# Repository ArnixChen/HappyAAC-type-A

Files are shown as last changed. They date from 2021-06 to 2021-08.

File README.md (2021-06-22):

# HappyAAC-type-A
## An open-source main-board to make AAC device makers Happy ;)
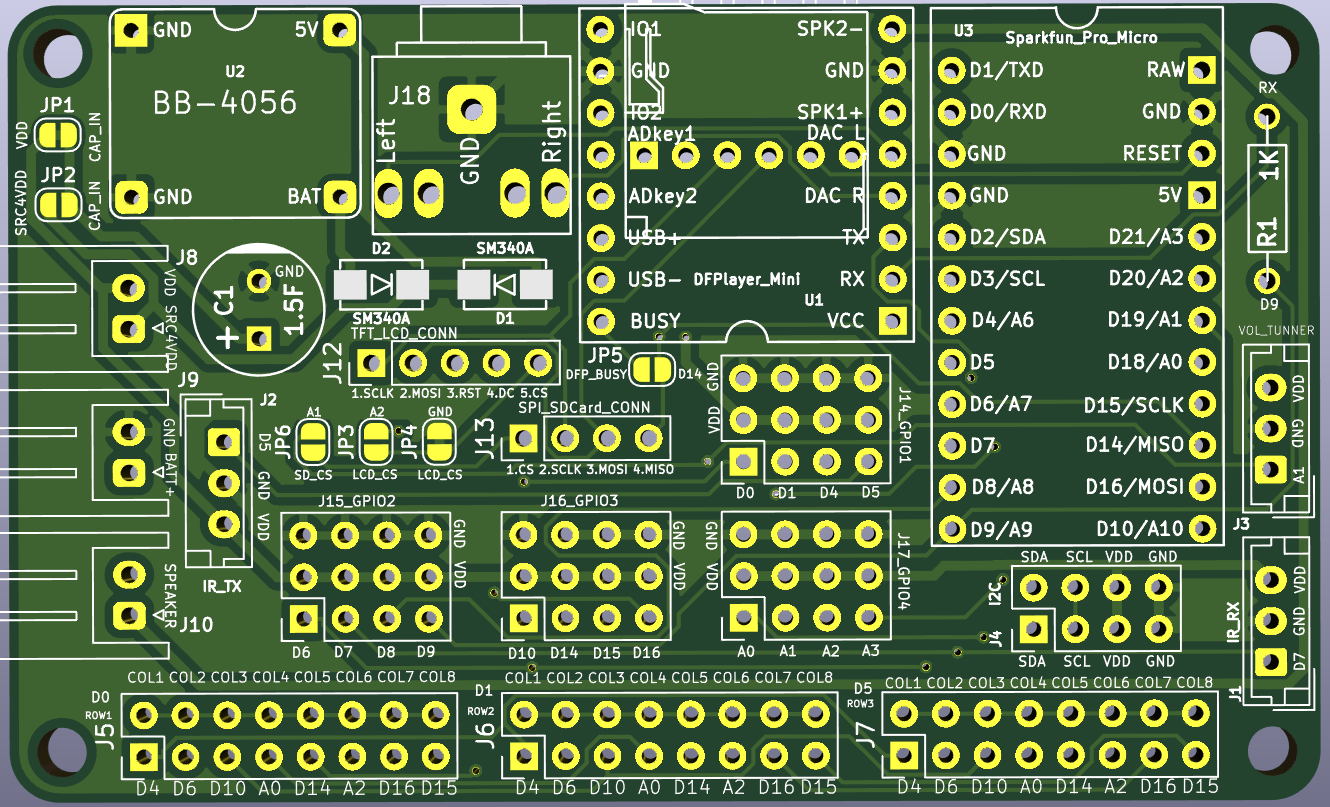
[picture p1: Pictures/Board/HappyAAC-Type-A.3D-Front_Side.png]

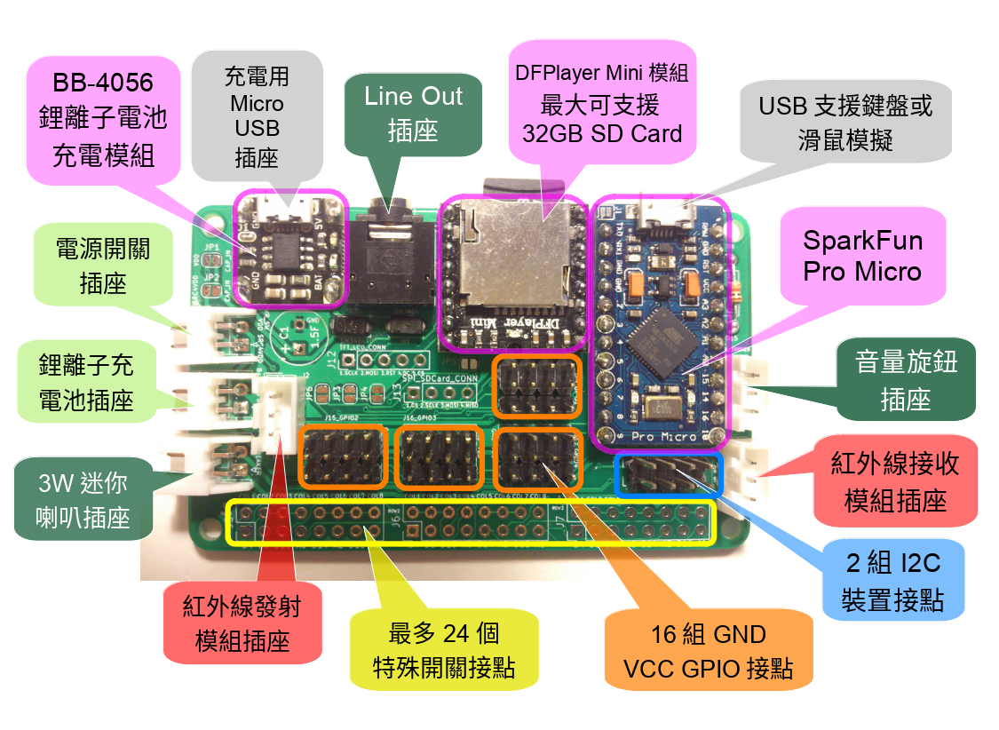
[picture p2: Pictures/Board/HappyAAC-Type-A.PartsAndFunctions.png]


## HappyAAC type A
#### 尺寸 8cm x 5cm 角落圓孔直徑 2.86mm
#### 它是一塊針對AAC溝通需求設計的開放電路板,使用者只要把必要的元件焊上電路板,就可以開始動手實作各種功能,免去手工連接大量線路的困難。

1. 使用 Sparkfun Pro Micro控制板, 支援鍵盤或滑鼠模擬功能
2. 內建 BB-4056 鋰電池充電模組線路,有插座可接鋰池及充電
3. 內建 DFPlayer Mini MP3 模組線路,內含一組音訊Line Out 用的插座,可接擴音喇叭,另有一組最大3W迷喇叭接插座
4. 一組音量旋鈕插座
5. 支援最多24個按鈕或特殊開關接點(沒有與其他功能衝突時)
6. 兩組獨立I2C裝置接點
7. 紅外線接收接座, 可以接遙控訊號
8. 紅外線發射接座,可以遙控其他的裝置
9. 留有16組GPIO +VCC+GND 接點,滿足特殊用途的需求
10. 它使用KiCad (open source)電路軟體設計, 並提供原始檔, 可以自己修改設計。

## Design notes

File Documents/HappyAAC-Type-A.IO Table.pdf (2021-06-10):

## IO使用表

Page 1

模組 PIN | Pro Micro 腳位代號 | PINs can do Interrupt wakeup | PINs can do Software Serial | ICSP 功能 | Keypad 功能 | DFPlayer Mini | Volume Tunner conn | I2C conn | IR Receiver conn | IR Transmitter conn | TFT LCD conn | SDCard Conn
1 | D1/TXD | D1 | | | ROW2
2 | D0/RXD | D0 | | | ROW1
3 | GND
4 | GND
5 | D2/SDA | D2 | | | | | | 1 SDA
6 | D3/SCL | D3 | | | | | | 2 SCL
7 | D4/A6 | | | | COL1
8 | D5 | | | | ROW3 | | | | | 1 IR_SEND
9 | D6/A7 | | | | COL2
10 | D7 | D7 | | | | | | | 1 IR_RECV
11 | D8/A8 | | D8 | | | DFP_TX
12 | D9/A9 | | D9 | | | DFP_RX
13 | D10/A10 | | D10 | | COL3
14 | D16/MOSI | | D16 | 4 MOSI | COL7 | | | | | | 4 LCD_MOSI | 3 SD_MOSI
15 | D14/MISO | | D14 | 1 MISO | COL5 | DFP_BUSY | | | | | | 4 SD_MISO
16 | D15/SCLK | | D15 | 3 SCLK | COL8 | | | | | | 3 LCD_SCLK | 2 SD_SCLK
17 | D18/A0 | | | | COL4
18 | D19/A1 | | | | | | 1 VOLUME_TUNNER | | | | | 1 SD_CS
19 | D20/A2 | | | | COL6 | | | | | | 7 LCD_CS
20 | D21/A3 | | | | | | | | | | 6 LCD_DC
21 | VCC | | | 2 VDD | | | 3 VDD | 3 VDD | 3 VDD | 3 VDD | 2 VDD | 5 VDD
22 | RESET | | | 5 RESET | e | | | | | | 5 RST
23 | GND | | | 6 GND | | | 2 GND | 4 GND | 2 GND | 2 GND | 1 GND | 6 GND
24 | RAW

## 表示未使用

Updated on 2021.0611

## 獨家使用,沒有衝突問題 有衝突, 只能擇一使用 有衝突, 只能擇一使用,但其中一方使用率低

## HappyAAC-Type-A-2c IO使用表

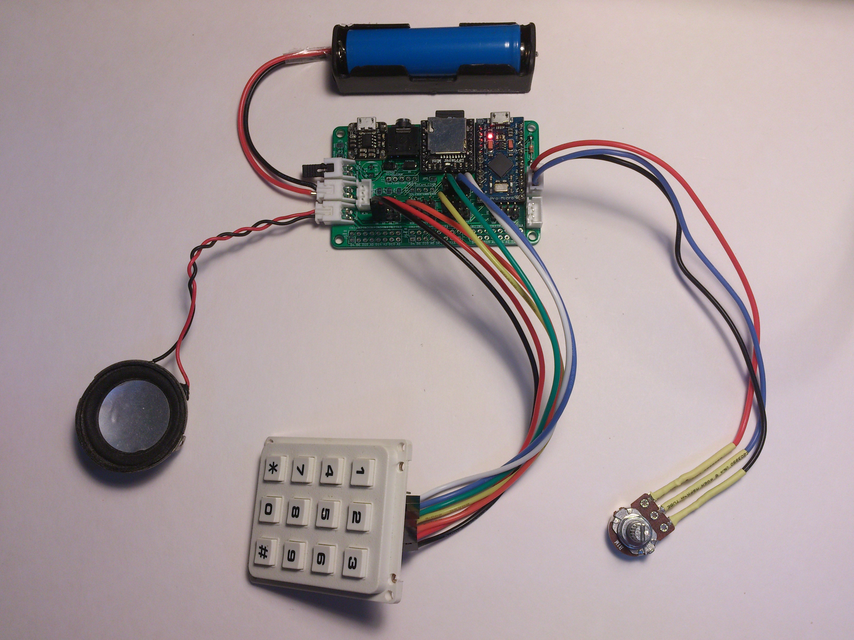
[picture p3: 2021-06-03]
Pictures/Application_Examples/phoneBox/Example_of_phoneBox.jpg

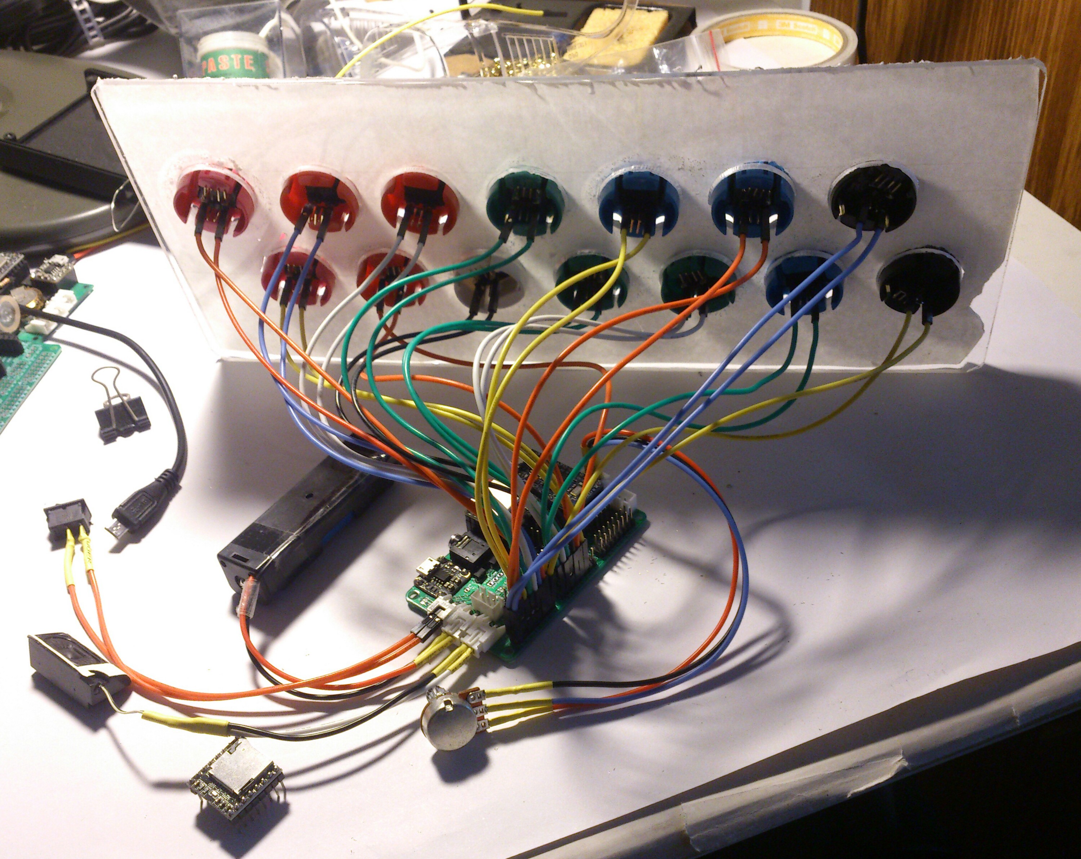
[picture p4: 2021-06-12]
Pictures/Application_Examples/Electric_Recorder/Electric_Recorder2.jpg

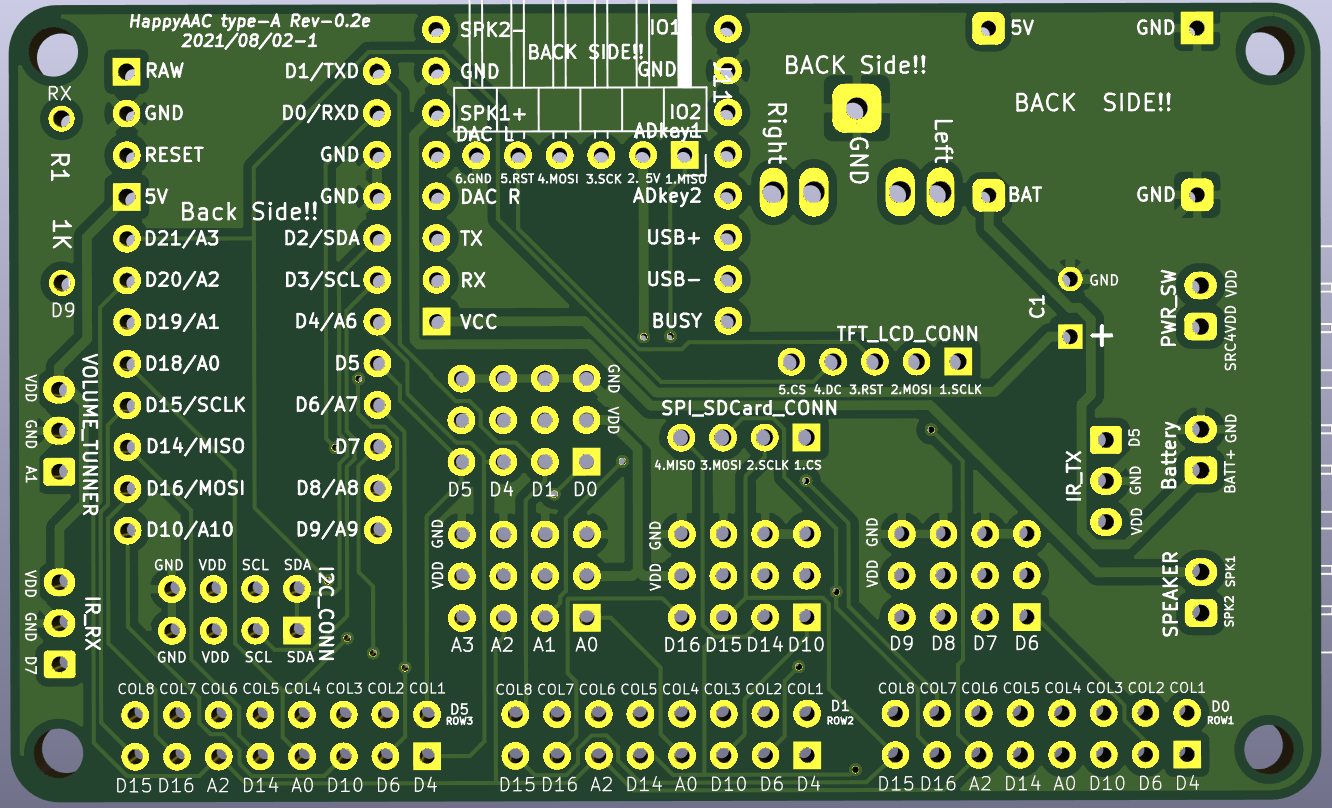
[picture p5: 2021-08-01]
Pictures/Board/HappyAAC-Type-A.3D-Back-Side.png

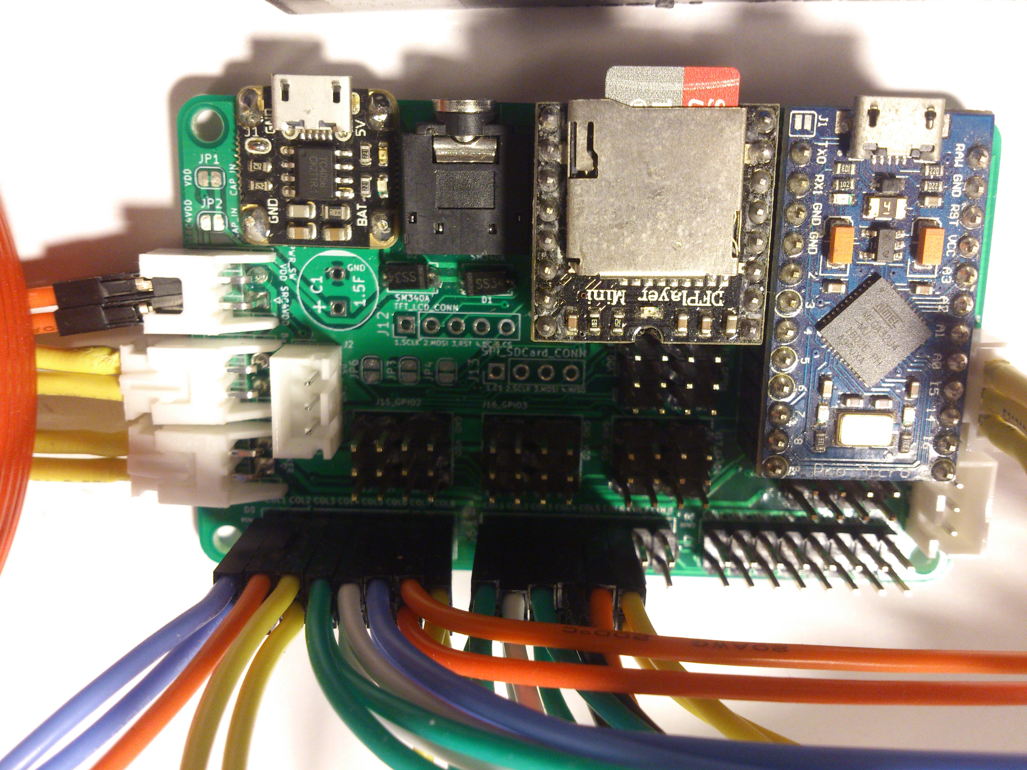
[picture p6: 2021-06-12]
Pictures/Application_Examples/Electric_Recorder/Electric_Recorder3.jpg

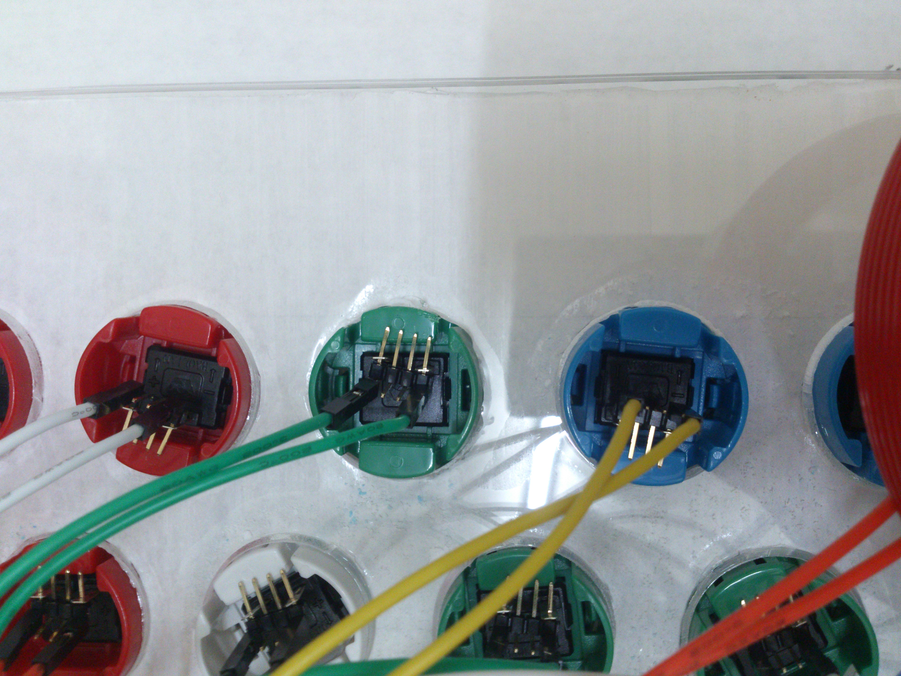
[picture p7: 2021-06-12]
Pictures/Application_Examples/Electric_Recorder/Eletric_Recorder4.jpg

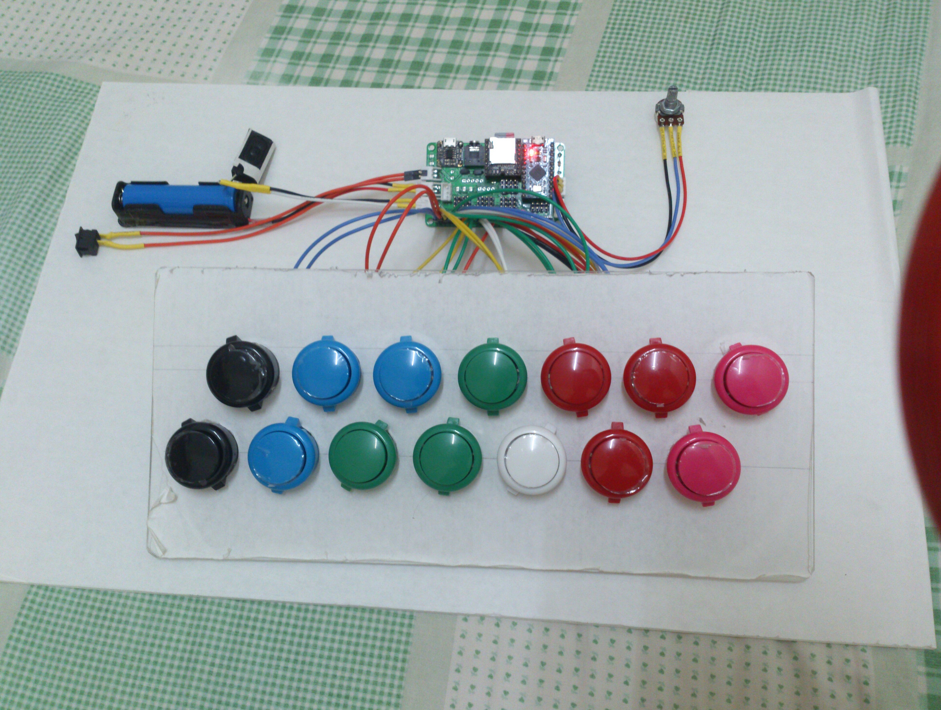
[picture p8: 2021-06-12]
Pictures/Application_Examples/Electric_Recorder/Electric_Recorder1.jpg

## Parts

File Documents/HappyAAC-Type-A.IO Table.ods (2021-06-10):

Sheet: IO使用表
模組 PIN | MCU 腳位 | Pro Micro 腳位代號 | PINs can do Interrupt wakeup | PINs can do Software Serial | ICSP 功能 | Keypad 功能 | DFPlayer Mini | Volume Tunner conn | I2C conn | IR Receiver conn | IR Transmitter conn | TFT LCD conn | SDCard Conn
1 |  | D1/TXD | D1 |  |  | ROW2
2 |  | D0/RXD | D0 |  |  | ROW1
3 |  | GND
4 |  | GND
5 |  | D2/SDA | D2 |  |  |  |  |  | 1 SDA
6 |  | D3/SCL | D3 |  |  |  |  |  | 2 SCL
7 |  | D4/A6 |  |  |  | COL1
8 |  | D5 |  |  |  | ROW3 |  |  |  |  | 1 IR_SEND
9 |  | D6/A7 |  |  |  | COL2
10 |  | D7 | D7 |  |  |  |  |  |  | 1 IR_RECV
11 |  | D8/A8 |  | D8 |  |  | DFP_TX
12 |  | D9/A9 |  | D9 |  |  | DFP_RX
13 |  | D10/A10 |  | D10 |  | COL3
14 |  | D16/MOSI |  | D16 | 4 MOSI | COL7 |  |  |  |  |  | 4 LCD_MOSI | 3 SD_MOSI
15 |  | D14/MISO |  | D14 | 1 MISO | COL5 | DFP_BUSY |  |  |  |  |  | 4 SD_MISO
16 |  | D15/SCLK |  | D15 | 3 SCLK | COL8 |  |  |  |  |  | 3 LCD_SCLK | 2 SD_SCLK
17 |  | D18/A0 |  |  |  | COL4
18 |  | D19/A1 |  |  |  |  |  | 1 VOLUME_TUNNER |  |  |  |  | 1 SD_CS
19 |  | D20/A2 |  |  |  | COL6 |  |  |  |  |  | 7 LCD_CS
20 |  | D21/A3 |  |  |  |  |  |  |  |  |  | 6 LCD_DC
21 |  | VCC |  |  | 2 VDD |  |  | 3 VDD | 3 VDD | 3 VDD | 3 VDD | 2 VDD | 5 VDD
22 |  | RESET |  |  | 5 RESET | e |  |  |  |  |  | 5 RST
23 |  | GND |  |  | 6 GND |  |  | 2 GND | 4 GND | 2 GND | 2 GND | 1 GND | 6 GND
24 |  | RAW
 |  |  | 表示未使用
 |  |  | 獨家使用,沒有衝突問題
 |  |  | 有衝突, 只能擇一使用
 |  |  | 有衝突, 只能擇一使用,但其中一方使用率低
 |  |  |  |  |  | HappyAAC-Type-A-2c IO使用表 |  |  |  |  | Updated on 2021.0611

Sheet: Bill Of Materials
編號 | 數量 | 參考記號 | 元件名稱 | 參考單價 | 總價 | 參考來源 | 說明
1 | 1 | U1 | DFPlayer Mini (非YX5200-24SS) | 63 | 63 | 露天 宇倉電子 Allen_6833 | 非YX5200-24SS版有支援 Total Folders 功能,但反應速度較 YX5200-24SS 慢
2 | 1 | U2 | BB-4056 | 15 | 15 | 露天 blkbox.me blackboxstudio
3 | 1 | U3 | Sprakfun Pro Micro 5v/16MHz | 150 | 150 | 露天 鈺瀚網舖 yuhhann_online
4 | 1 | R1 | 1KΩ 電阻 | 0.2 | 0.2 | 今華電子
5 | 1 | C1 | 1.5F 電容 | 33 | 33 | 不確定 | 非必要零件(供電不穩時才考慮使用)
6 | 3 | J1,J2,J3 | 2.50mm JST 01x03pin Vertical 公 | 2 | 6 | 今華電子
7 | 1 | J4 | 2.54mm PinHeader 02x04pin 180度 |  | 0 | 今華電子 | I2C
8 | 3 | J5,J6,J7 | 2.54mm PinHeader 02x08pin 90度 |  | 0 | 今華電子 | For Keypad Connector
9 | 1 | J8 | 2.50mm JST 01x02pin Horizontal 公 | 1 | 1 | 今華電子 | Speaker Connector
10 | 1 | J14 | 2.50mm JST 01x02pin Horizontal 公 | 1 | 1 | 今華電子 | Power Switch Connector
11 | 1 | J15 | 2.50mm JST 01x02pin Horizontal 公 | 1 | 1 | 今華電子 | Battery Connector
12 | 1 | J9 | 3.5mm Stereo Audio Jack 4pin+Ground | 10 | 10 | 今華電子 | Audio Jack
13 | 1 | J11 | 2.54mm 01x06pin 排針母座 | 3 | 3 | 今華電子 | ICSP Connector
14 | 1 | J12 | 2.54mm 01x05pin 排針母座 | 2.5 | 2.5 | 今華電子 | SPI connector for TFT LCD
15 | 4 | J13,J17,J19,J21 | 2.54mm PinHeader 03x04pin 180度 |  | 0 | 今華電子 | General GPIO Connector
16 | 2 | D1,D2 | SM340A | 5.4 | 10.8 | 露天 ju_el | 防止電流倒灌造成逆向充電
17 | 1 | J18 | Stereo Audio Jack Socket | 10 | 10 | 今華電子 | Line out 插座
18 | 1 | PCB | HappyAAC type A PCB | 60 | 60 |  | 無鉛鍍錫拼版與不拼版價差可能1倍
19 |  |  |  |  | 0
20 |  |  |  |  | 0
21 |  | 價格需要再調查 |  |  | 0
 |  |  |  | 合計 | 366.5

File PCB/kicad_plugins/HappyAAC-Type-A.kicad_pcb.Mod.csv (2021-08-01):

Reference | RefVisible | Value | ValVisible | xPos | yPos | Orientation | LayerName | IsFlipped
U2 | True | BB-4056 | True | 73990200.0 | 34036000.0 | 0.0 | F.Cu | False
U1 | True | DFPlayer_Mini | True | 105105000.0 | 35941000.0 | 180.0 | F.Cu | False
J11 | True | ICSP | True | 98856800.0 | 35991800.0 | 90.0 | F.Cu | False
J10 | True | SPEAKER | True | 67445400.0 | 61465900.0 | 270.0 | F.Cu | False
J9 | True | Batt | True | 67445400.0 | 52767300.0 | 270.0 | F.Cu | False
J8 | True | PWR_SW | True | 67445400.0 | 44005200.0 | 270.0 | F.Cu | False
U3 | True | Sparkfun_Pro_Micro | True | 125248000.0 | 43586400.0 | 0.0 | F.Cu | False
J18 | True | AudioJack | True | 88366600.0 | 33172400.0 | 270.0 | F.Cu | False
C1 | True | 1.5F | True | 75387200.0 | 45351700.0 | 90.0 | F.Cu | False
J1 | True | IR_RX | True | 137004000.0 | 66941100.0 | 90.0 | F.Cu | False
J2 | True | IR_TX | True | 73228200.0 | 53403500.0 | 270.0 | F.Cu | False
J3 | True | VOL_TUNNER | True | 137004000.0 | 55206900.0 | 90.0 | F.Cu | False
R1 | True | 1K | True | 136804000.0 | 38705700.0 | 90.0 | F.Cu | False
J4 | True | I2C | True | 122542000.0 | 64912200.0 | 90.0 | F.Cu | False
J5 | True | ROW1 | True | 68306400.0 | 72585900.0 | 90.0 | F.Cu | False
J14_GPIO1 | True | Conn_03x04_Odd_Even_VSG | True | 104877000.0 | 52123300.0 | 90.0 | F.Cu | False
J15_GPIO2 | True | Conn_03x04_Odd_Even_VSG | True | 78066900.0 | 61645800.0 | 90.0 | F.Cu | False
J16_GPIO3 | True | Conn_03x04_Odd_Even_VSG | True | 91471900.0 | 61633100.0 | 90.0 | F.Cu | False
J17_GPIO4 | True | Conn_03x04_Odd_Even_VSG | True | 104877000.0 | 61633100.0 | 90.0 | F.Cu | False
D1 | True | SM340A | True | 90384300.0 | 43841000.0 | 180.0 | F.Cu | False
D2 | True | SM340A | True | 82854800.0 | 43841000.0 | 0.0 | F.Cu | False
J12 | True | TFT_LCD | True | 82219800.0 | 48602900.0 | 90.0 | F.Cu | False
JP1 | True | SolderJumper_2_Bridged | True | 63182500.0 | 34683700.0 | 0.0 | F.Cu | False
JP2 | True | SolderJumper_2_Open | True | 63220600.0 | 38938200.0 | 0.0 | F.Cu | False
JP3 | True | SolderJumper_2_Open | True | 82510600.0 | 53403500.0 | 90.0 | F.Cu | False
JP4 | True | SolderJumper_2_Bridged | True | 86357400.0 | 53403500.0 | 90.0 | F.Cu | False
JP5 | True | SolderJumper_2_Open | True | 99326700.0 | 49034700.0 | 0.0 | F.Cu | False
J13 | True | SDCard_Conn | True | 91478100.0 | 53213000.0 | 90.0 | F.Cu | False
JP6 | True | SolderJumper_2_Open | True | 78663800.0 | 53403500.0 | 90.0 | F.Cu | False
J6 | True | ROW2 | True | 91468700.0 | 72585900.0 | 90.0 | F.Cu | False
J7 | True | ROW3 | True | 114631000.0 | 72585900.0 | 90.0 | F.Cu | False

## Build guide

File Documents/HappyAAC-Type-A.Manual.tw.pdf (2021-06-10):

# HappyAAC type A

## 說明書

2021/06/09 更新

免責聲明： HappyAAC type A, 以下簡稱 HappyAAC 。
HappyAAC 之設計僅在於提供大眾一個設計之參考範例、應用之構思基 礎。任何運用 HappyAAC 設計的人士，必須自行承擔一切風險。

HappyAAC 的開發者不會負責任何運用 HappyAAC 設計而導致之損 失，亦不會作出任何默認的擔保。 HappyAAC 不保證其設計正確無誤 , 也不保證其設計不存在風險。我們不對運用 HappyAAC 者的財產、身、 心損害負有賠償責任。

## 1. HappyAAC type A 介紹

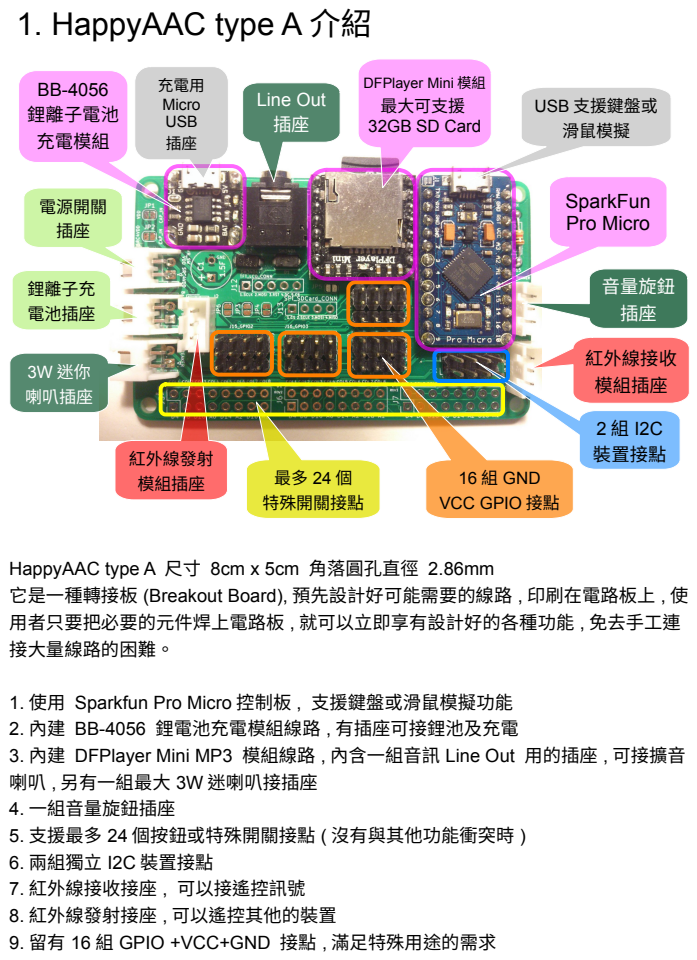
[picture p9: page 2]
SparkFun Pro Micro; 音量旋鈕 插座; 紅外線接收 模組插座; 紅外線發射; 裝置接點; 模組插座; 特殊開關接點; 電源開關 插座; 鋰離子充 電池插座; 3W 迷你 喇叭插座; Line Out 插座; BB-4056 鋰離子電池 充電模組; 充電用 Micro USB 插座; USB 支援鍵盤或 滑鼠模擬

DFPlayer Mini 模組
最大可支援
32GB SD Card

16 組 GND
VCC GPIO 接點

HappyAAC type A 尺寸 8cm x 5cm 角落圓孔直徑 2.86mm
它是一種轉接板 (Breakout Board), 預先設計好可能需要的線路 , 印刷在電路板上 , 使
用者只要把必要的元件焊上電路板 , 就可以立即享有設計好的各種功能 , 免去手工連
接大量線路的困難。

1. 使用 Sparkfun Pro Micro 控制板 , 支援鍵盤或滑鼠模擬功能
2. 內建 BB-4056 鋰電池充電模組線路 , 有插座可接鋰池及充電
3. 內建 DFPlayer Mini MP3 模組線路 , 內含一組音訊 Line Out 用的插座 , 可接擴音
喇叭 , 另有一組最大 3W 迷喇叭接插座
4. 一組音量旋鈕插座
5. 支援最多 24 個按鈕或特殊開關接點 ( 沒有與其他功能衝突時 )
6. 兩組獨立 I2C 裝置接點
7. 紅外線接收接座 , 可以接遙控訊號
8. 紅外線發射接座 , 可以遙控其他的裝置
9. 留有 16 組 GPIO +VCC+GND 接點 , 滿足特殊用途的需求

1. SparkFun Pro Micro 5v,16Mhz x1
2. DFPlayer Mini x1
3. BB-4056 鋰電池充電模組 x1
4. SM340A schottky barrier rectifiers SMD x2
5. 1K 歐姆電阻 x1
6. JST-XH 2-pin 連接器 ( 水平 或 垂直 可自選 ) 公頭 x3
7. JST-XH 2-pin 連接器 母頭 x3
8. JST-XH 3-pin 連接器 垂直 公頭 x3
9. Phone Jack 耳機插座 3.5mm 5-pin x1
10. 間距 2.54mm 40-pin 單排排針母座 易折型 x1
11. 間距 2.54mm 40-pin 雙排排針 (180 度 ) 易折型 x2
12. 最大 3 W 的 4 或 8 歐姆 喇叭 x1
13. JST-XH 端子頭 x15
14. MicroSD Card x1 (SD 卡大小 , 視使用的音檔總容量而定）
15. 開關 ( 電源用類型不拘 ) x1

16.18650 鋰離子電池 ( 為了安全 , 務必使用大廠電池 ) x1

17. 18650 電池槽 x1

PS. 第 6 項、第 8 項 , 不一定非使用 JST-XH 連接器不可 , 也可以用 2.54mm 排針代替。 只是這樣就沒有防呆的保護功能 ( 開關插座及喇叭插座沒有極性的問題 , 可以不用 JST-XH)
如果有意使用 JST-XH 連接器的話 , 強烈建議 - 要準備一支像 KELY YS-09A/E 的 JST-XH
專用壓接鉗 , 不然使用一般的工具 , 想要把 JST 端子壓好是很困難的。

## 3. HappyAAC type A 零件表

鋰電池本身就存在可能發生
爆炸的風險，使用者務必慎
選品質可靠的廠牌來源，並
在使用上特別小心。

## 4. HappyAAC type A 的正反面辨識

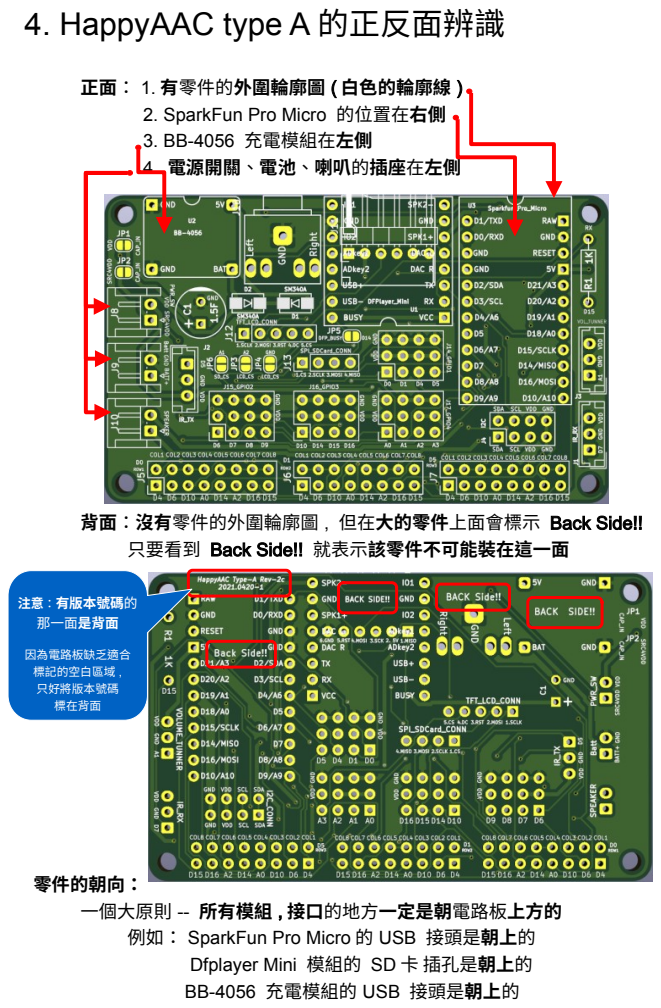
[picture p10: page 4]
注意：有版本號碼的 那一面是背面; 因為電路板缺乏適合 標記的空白區域 , 只好將版本號碼 標在背面

正面： 1. 有零件的外圍輪廓圖 ( 白色的輪廓線 )

2. SparkFun Pro Micro 的位置在右側
3. BB-4056 充電模組在左側
4. 電源開關、電池、喇叭的插座在左側

背面：沒有零件的外圍輪廓圖 , 但在大的零件上面會標示 Back Side!!
只要看到 Back Side!! 就表示該零件不可能裝在這一面

零件的朝向：
一個大原則 -- 所有模組 , 接口的地方一定是朝電路板上方的
例如： SparkFun Pro Micro 的 USB 接頭是朝上的

Dfplayer Mini 模組的 SD 卡 插孔是朝上的
BB-4056 充電模組的 USB 接頭是朝上的

## 5.HappyAAC type A 焊接順序 part I

1. 正面 SM340A schottky barrier rectifiers SMD
1. 先在 pad 塗上助焊劑。

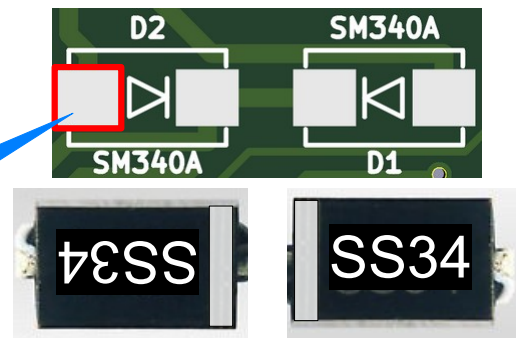
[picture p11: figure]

(pad: 指電路板上用來接通元件與電路板的表面區域 , 上焊錫的區域）
2. 將 SM340A 依圖示方向擺置在 pad 上 ( 有白線的那一側要朝中央 )
3. 烙鐵尖端沾少許焊錫 , 將沾有焊錫的部位靠向其中一顆 SM340A 的 側邊金屬與 pad 交界的地方 ( 最好用空出來的另一隻手拿夾子夾住 SMA340A, 使用它不會一碰就移位 ), 待焊錫被吸入 SM340A 底部 , 並覆蓋 側邊金屬部位 , 即完成該側的焊接 , 繼續完成同顆另一端的焊接。
4. 依同樣 1~3 步驟完成另一顆 SMA340A 的焊接。
2. 背面 ICSP 接頭 ( 正面電路板上畫有 ICSP 針腳輪廓圖是錯的 , 不要理它 , 應該畫在背面 )
1. 取出 40-pin 單排排針母座 , 用尖嘴鉗折出長度 6-pin 的片段。

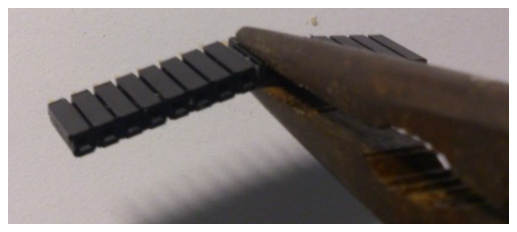
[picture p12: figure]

2. 剪下一片雙面膠貼滿排針母座的其中一面 , 用刀片割去多餘的雙面膠。
3. 利用桌面 , 稍微施力將接腳（折向貼有雙面膠的一側）折彎 90 度。
4. 撕開雙面膠 , 將此 6-pin ICSP 接頭貼在電路板背面的 ICSP 位置
針腳一一插入 6.GND 5.RST 4.MOSI 3.SCK 2.5V 1.MISO 標示上方
的焊孔。

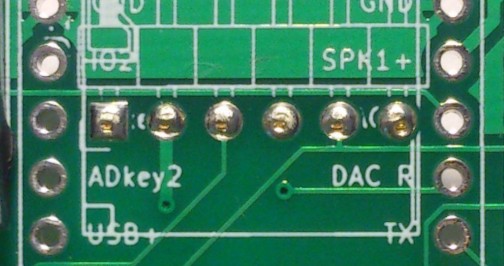
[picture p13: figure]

5. 在電路板背面 , 將每支針腳與焊孔相接部位確實焊接。
3. 正面 右上角 1K 歐姆電阻
4. BB-4056 鋰電池充電模組
注意：安裝前 , 要注意核對電路板上的輪廓圖 ,USB 接口朝向要跟輪廓圖 的半圓形方向一致 , 如果裝錯了 , 通電時可能會把模組燒壞。
5. 正面 Line Out 插座
1. 用斜口鉗將插座底部小圓突起一一剪去 ( 如此 , 插座在電路板上伸出來 的接腳才會夠長 ), 然後再插上電路板進行焊接。

pad

※ 如果想要以後可以把 Pro Micro 及 DFPlayer Mini 拆下來再利用 , 可以把下面的
步驟 2 改成：在電路板 上原本給 Pro Micro 及 DFPlayer Mini 用的焊孔上 , 各焊 兩排排針母座 , 再將已焊好針腳的 Pro Micro 及 DFPlayer Mini 插到排針母
座上。其中
SparkFun Pro Micro 要用 12-pin 的排針母座 x2
DFPlayer Mini 要用 8-pin 的排針母座 x2

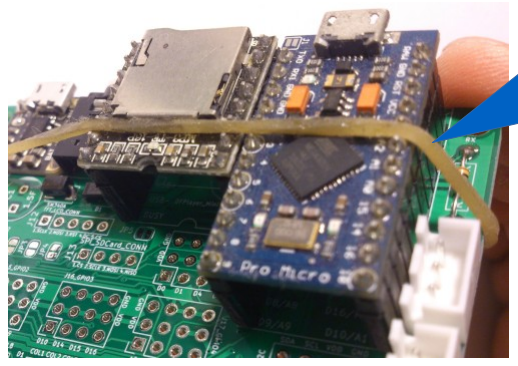
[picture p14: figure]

5. SparkFun Pro Micro 5v,16Mhz
注意：安裝前 , 要注意核對電路板上的輪廓圖 ,USB 接口朝向要跟輪廓圖的半 圓形方向一致 , 如果裝錯了 , 通電時可能會把模組燒壞。
1. 為 SparkFun Pro Micro 的兩側焊上排針 , 焊之前要確認每支排針的塑膠部 份都有確實頂到 SparkFun Pro Micro 的電路板 , 每支針腳高度大致相同。 如果沒有頂到底可能會產生歪邪的問題 , 將來要插到 type A 電路板可能會有 困難。
2. 將焊好針腳的 SparkFun Pro Micro 小心插到 type A 電路板的正面孔位 ,
並確認每個部位都有確實貼緊電路板 , 然後逐一焊好與 type A 電路板接觸的 每一個接點。
6. DFPlayer Mini 模組
注意 1 ： 安裝前 , 要注意核對電路板上的輪廓圖 ,SD 卡接口朝向要朝外 , 模組上的半圓形缺口方向 , 要與輪廓圖的半圓形方向
一致 , 如果裝錯了 , 通電時可能會把模組燒壞。

注意 2 ：因為先前已在背面焊上 ICSP 的接頭 , 焊

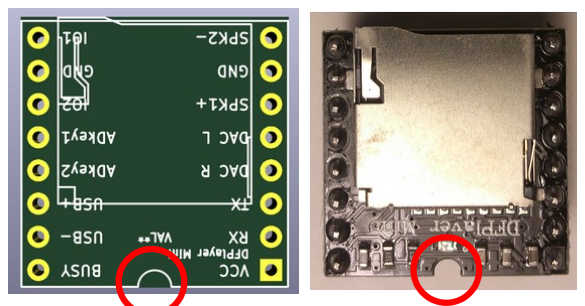
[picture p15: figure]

DFPlayer Mini 的針腳時的空間會顯得比較受限 , 容易造成焊錫溢出接觸別的 接點的情況 , 如果有的話務必要將它整理乾淨 , 接腳間訊號短路會不正常。

## 5. HappyAAC type A 焊接順序 part II

焊接排針母座時可以
先將模組插到排針母座上 ,
再整個插到電路板上 ,
用橡皮筋固定好 ,
最後進行焊接

## 5. HappyAAC type A 焊接順序 part III

7. 安裝 JST-XH 2pin 插座 , 也就左側的 電源開關、鋰電池插座、喇叭插座。 其中只有中間的鋰電池插座要注意極性 ( 正極在下方那一支腳 ), 不能插 錯 , 所以必須有防呆 , 請務必使用 JST-XH 2pin 插座 , 其它兩個則可以 用別的做法取代 ( 例如用間距 2.54mm 的排針代替 ) 。
如果您選的 JST-XH 插座形式是水平式的 , 像這樣 | , 那麼
建議在插座的下方貼上雙面膠 , 再插到電路板上焊接 , 可以讓插座與電 路板的附著更牢固。
8. 安裝 JST-XH 3pin 垂直插座 , 安裝時注意 , 不管插座是在左側還是右側 , 插座的缺口都是朝內的 ( 朝電路板中央的 ) 。
( 第 2 頁中的圖 , 紅外線發射模組插座安裝方向是錯的 )
9. 安裝 16 組 GPIO 的排針。取出間距 2.54mm 40-pin 雙排排針 , 切出
「每一排只 3 支針 ( 共 6 支針 ) 」的雙排排針 8 個。兩兩一組地插在電 路板上。焊接時可以用單排或雙排的排針母座 , 幫助這兩兩一組的排針 固定 , 再用橡皮筋綁在電路板上 , 如此翻到背面焊接就會牢固許多。

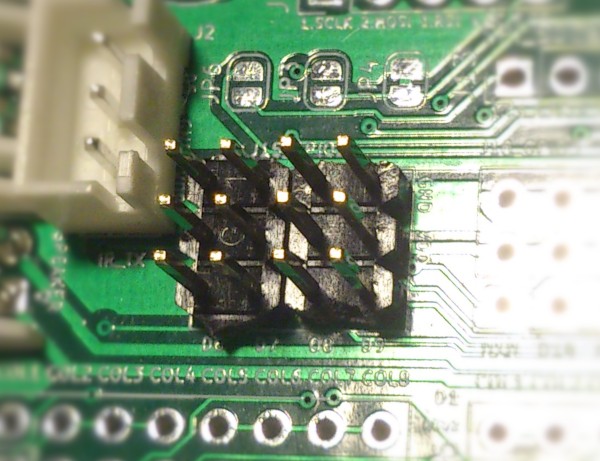
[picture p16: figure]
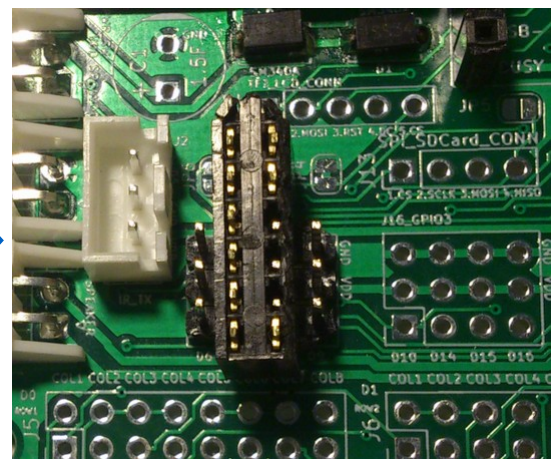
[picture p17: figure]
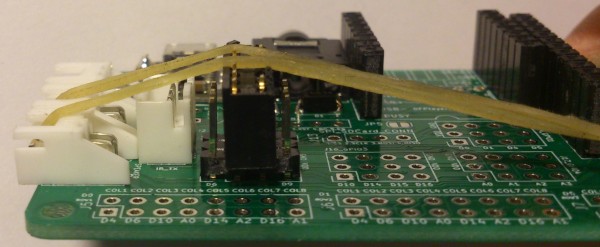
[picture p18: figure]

反覆這樣的步驟 , 四次就可以將這 16 組
(4 個一群 )GPIO 接點全部焊好了。

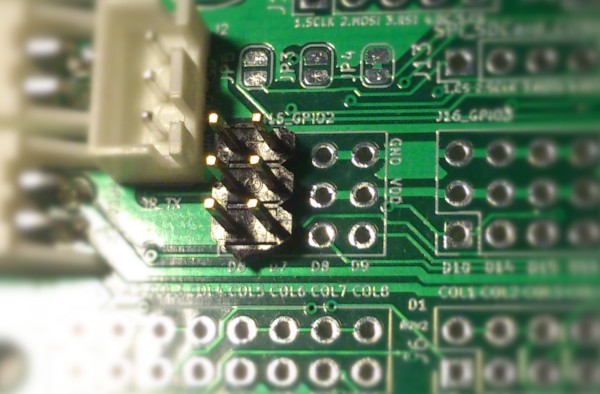
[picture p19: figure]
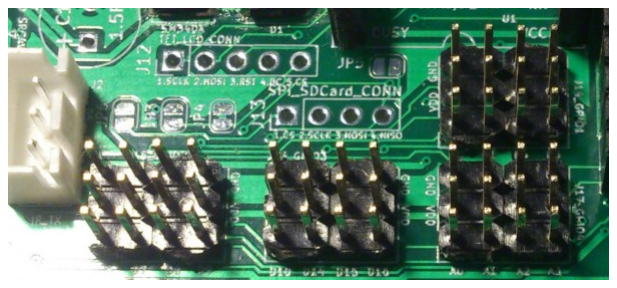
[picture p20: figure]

10. 將雙排排針切成 I2C 接點 ( 每排 4 支針 ) 及 24 個特殊開關 ( 每排 8 支 針 ) 的所需的長度 , 類似前述 GPIO 的做法 , 即可將剩餘的接點完成。

缺口

## 6. HappyAAC type A 程式載入方法

1. 準備 USBasp 燒錄器
2. 準備 ICSP 燒錄線

## 7. HappyAAC type A 基本測試

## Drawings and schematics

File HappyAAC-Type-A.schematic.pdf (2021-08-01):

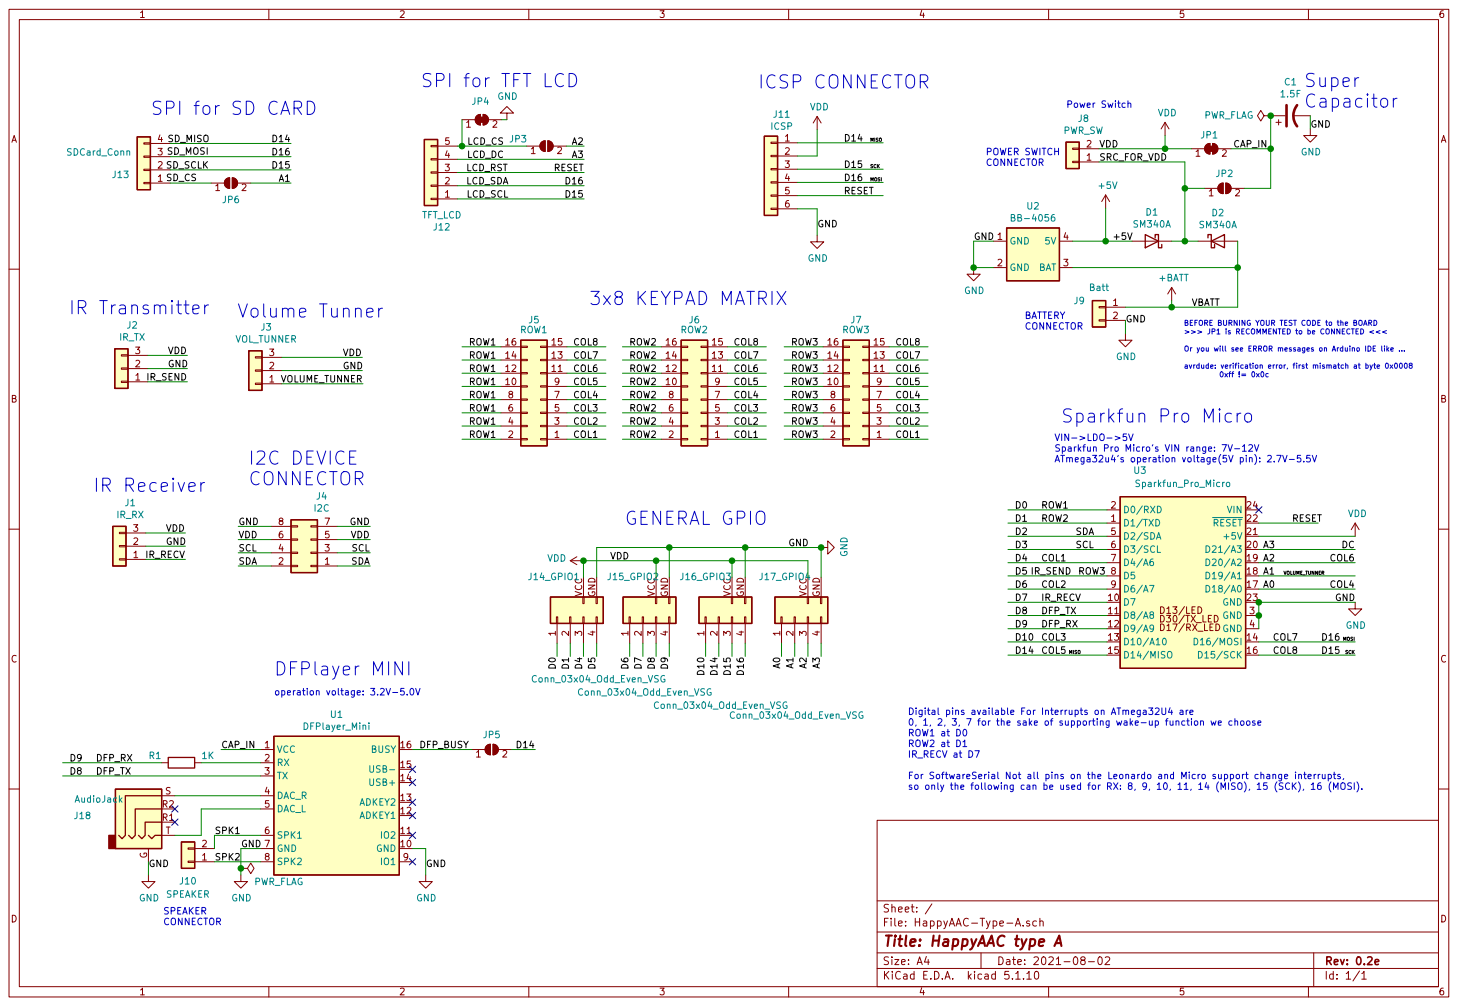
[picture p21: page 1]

0xff != 0x0c SPI for TFT LCD

Capacitor SPI for SD CARD
IR Transmitter SPEAKER

BEFORE BURNING YOUR TEST CODE to the BOARD
>>> JP1 is RECOMMENTED to be CONNECTED <<< Or you will see ERROR messages on Arduino IDE like ... avrdude: verification error, first mismatch at byte 0x0008

VIN->LDO->5V
Sparkfun Pro Micro's VIN range: 7V-12V
ATmega32u4's operation voltage(5V pin): 2.7V-5.5V

Digital pins available For Interrupts on ATmega32U4 are
0, 1, 2, 3, 7 for the sake of supporting wake-up function we choose ROW1 at D0 ROW2 at D1

IR_RECV at D7 For SoftwareSerial Not all pins on the Leonardo and Micro support change interrupts,

so only the following can be used for RX: 8, 9, 10, 11, 14 (MISO), 15 (SCK), 16 (MOSI).

File: HappyAAC-Type-A.sch Sheet: / G
GND
J10 SPEAKER

Id: 1/1 Title: HappyAAC type A

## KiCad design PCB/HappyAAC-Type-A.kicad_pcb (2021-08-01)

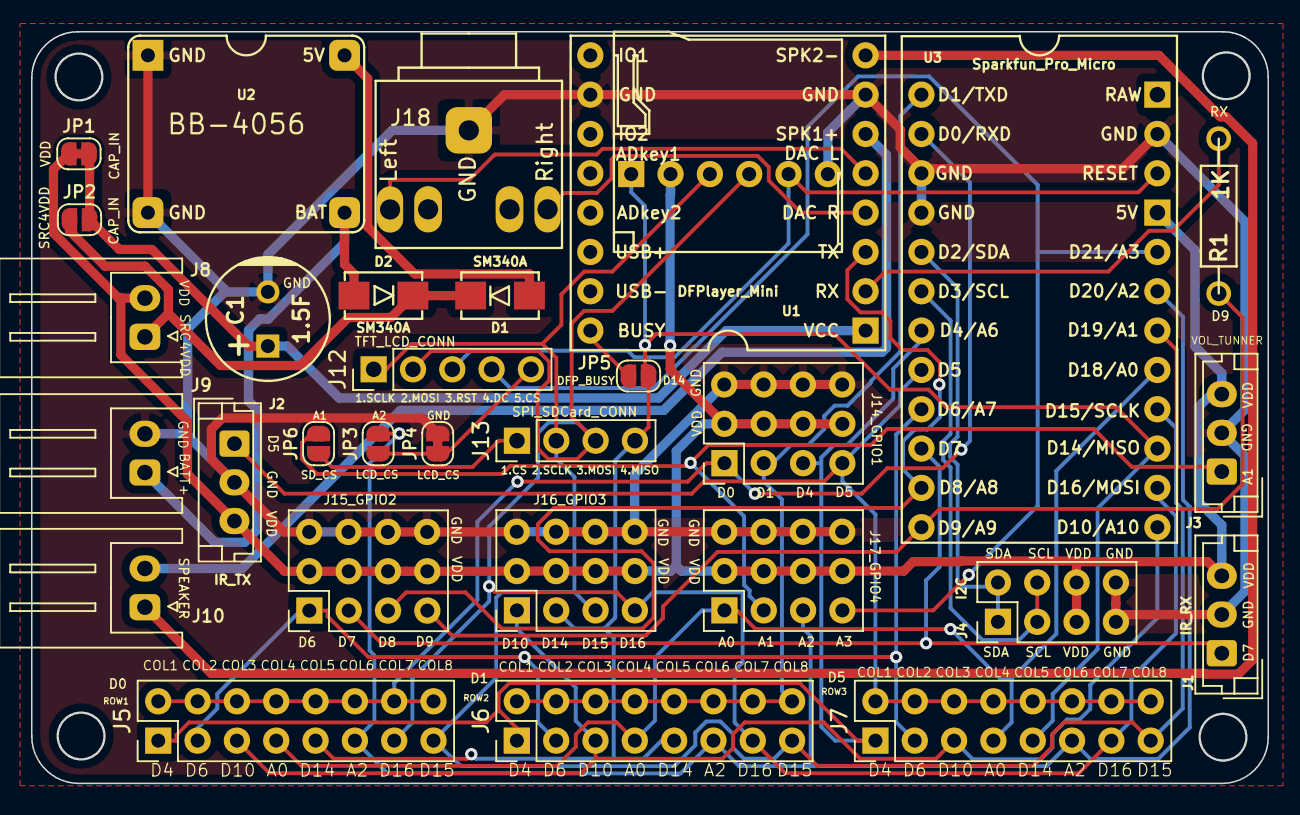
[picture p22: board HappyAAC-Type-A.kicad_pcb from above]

Board: 2 copper layers, 79.9 x 48.6 mm, 31 parts (0 on the bottom side), 33 nets.

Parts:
C1: 1.5F; CAP_pol_DIP_D8mm
D1, D2: SM340A; SMA_DO214AC_M_SM340A
J1: IR_RX; JST_EH_B3B-EH-A_1x03_P2.50mm_Vertical
J2: IR_TX; JST_EH_B3B-EH-A_1x03_P2.50mm_Vertical
J3: VOL_TUNNER; JST_EH_B3B-EH-A_1x03_P2.50mm_Vertical
J4: I2C; PinHeader_2x04_P2.54mm_Vertical_PadHole0.9mm
J5: ROW1; PinHeader_2x08_P2.54mm_Vertical
J6: ROW2; PinHeader_2x08_P2.54mm_Vertical
J7: ROW3; PinHeader_2x08_P2.54mm_Vertical
J8: PWR_SW; PEC-2503-2H.JST_XH_S2B-XH-A_1x02_P2.50mm_Horizontal
J9: Batt; PEC-2503-2H.JST_XH_S2B-XH-A_1x02_P2.50mm_Horizontal
J10: SPEAKER; PEC-2503-2H.JST_XH_S2B-XH-A_1x02_P2.50mm_Horizontal
J11: ICSP; ICSP_PinHeader_1x06_P2.54mm_Horizontal
J12: TFT_LCD; PinHeader_1x05_P2.54mm_Vertical
J13: SDCard_Conn; PinHeader_1x04_P2.54mm_Vertical
J14_GPIO1, J15_GPIO2, J16_GPIO3, J17_GPIO4: Conn_03x04_Odd_Even_VSG; PinHeader_3x04_P2.54mm_Vertical_PadHole0.9mm
J18: AudioJack; Jack_3.5mm_Arnix_5pin_AudioJack4_Ground_Horizontal
JP1, JP4: SolderJumper_2_Bridged; SolderJumper-2_P1.3mm_Bridged_RoundedPad1.0x1.5mm
JP2, JP3, JP5, JP6: SolderJumper_2_Open; SolderJumper-2_P1.3mm_Open_RoundedPad1.0x1.5mm
R1: 1K; RES_DIP_0.25W_10mm
U1: DFPlayer_Mini; DFPlayer_Mini_BigPad
U2: BB-4056
U3: Sparkfun_Pro_Micro; Sparkfun_Pro_Micro_BigPad

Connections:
+5V: D1.2, U2.4
+BATT: D2.2, J9.1, U2.3
/A0: J5.7, J6.7, J7.7, J17_GPIO4.1, U3.17
/A1: J3.1, J17_GPIO4.2, JP6.2, U3.18
/A2: J5.11, J6.11, J7.11, J17_GPIO4.3, JP3.2, U3.19
/A3: J12.4, J17_GPIO4.4, U3.20
/CAP_IN: C1.1, JP1.2, JP2.2, U1.1
/COL1: J5.1, J6.1, J7.1, J14_GPIO1.3, U3.7
/COL2: J5.3, J6.3, J7.3, J15_GPIO2.1, U3.9
/COL3: J5.5, J6.5, J7.5, J16_GPIO3.1, U3.13
/COL5: J5.9, J6.9, J7.9, J11.1, J13.4, J16_GPIO3.2, JP5.2, U3.15
/COL7: J5.13, J6.13, J7.13, J11.4, J12.2, J13.3, J16_GPIO3.4, U3.14
/COL8: J5.15, J6.15, J7.15, J11.3, J12.1, J13.2, J16_GPIO3.3, U3.16
/D0: J5.2, J5.4, J5.6, J5.8, J5.10, J5.12, J5.14, J5.16, J14_GPIO1.1, U3.2
/D1: J6.2, J6.4, J6.6, J6.8, J6.10, J6.12, J6.14, J6.16, J14_GPIO1.2, U3.1
/D2: J4.1, J4.2, U3.5
/D3: J4.3, J4.4, U3.6
/D5: J2.1, J7.2, J7.4, J7.6, J7.8, J7.10, J7.12, J7.14, J7.16, J14_GPIO1.4, U3.8
/D7: J1.1, J15_GPIO2.2, U3.10
/D8: J15_GPIO2.3, U1.3, U3.11
/D9: J15_GPIO2.4, R1.1, U3.12
/DFP_BUSY: JP5.1, U1.16
/LCD_CS: J12.5, JP3.1, JP4.1
/LCD_RST: J11.5, J12.3, U3.22
/SPK1: J10.2, U1.6
/SPK2: J10.1, U1.8
/SRC_FOR_VDD: D1.1, D2.1, J8.1, JP2.1
GND: C1.2, J1.2, J2.2, J3.2, J4.7, J4.8, J9.2, J11.6, J14_GPIO1.GND, J15_GPIO2.GND, J16_GPIO3.GND, J17_GPIO4.GND, J18.G, JP4.2, U1.7, U1.10, U2.1, U2.2, U3.3, U3.4, U3.23
unnamed: J13.1, JP6.1
unnamed: J18.S, U1.4
unnamed: J18.T, U1.5
unnamed: R1.2, U1.2
VDD: J1.3, J2.3, J3.3, J4.5, J4.6, J8.2, J11.2, J14_GPIO1.VCC, J15_GPIO2.VCC, J16_GPIO3.VCC, J17_GPIO4.VCC, JP1.1, U3.21

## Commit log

2021-06-03 Update HappyAAC-Type-A.說明.odg Add HappyAAC-Type-A.說明.pdf
2021-06-03 Move csv files to folder kicad_plugins
    [HappyAAC-Type-A.kicad_pcb.EdgeCuts.csv, HappyAAC-Type-A.kicad_pcb.Mod.csv, HappyAAC-Type-A.kicad_pcb.Text.csv]
2021-06-03 move pictures in root folder into folder pictures/Board
2021-06-03 Add pictures for showing HappyAAC-type-A main parts assembled
2021-06-03 Move documents to Documents folder
    [HappyAAC-Type-A.IO使用表.ods]
2021-06-03 Move PCB related files into PCB folder
    [AACMaker-2c-job.gbrjob, AACMaker-Type-A-2c-job.gbrjob, HappyAAC-Type-A-2c-B_Cu.gbr, HappyAAC-Type-A-2c-B_Mask.gbr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]
2021-06-03 Replace filename 'IO使用表' with 'IO Table'
    [HappyAAC-Type-A.IO Table.ods]
2021-06-03 Replace filename '說明' with 'Manual'
2021-06-04 update user's manual for traditional chinese -- add material list
2021-06-04 Add list of materials for HappyAAC type A.
2021-06-05 Update user's manual -- Add Soldering-Guide for significant parts.
2021-06-06 Update HappyAAC-type-A.3D-Front-Side.png (remove 3D through hole parts)
2021-06-06 Update HappyAAC-Type-A.3D-Back-Side.png (remove 3D through hole parts)
2021-06-06 1. Lower the picture resolution to make HappyAAC-Type-A.Manual.odg file small 2. Update Soldering guide section to part II
2021-06-06 Update J8 PWR_SW ,J9 BATT_SW ,J10 SPEAKER footprint association to JST_XH_S2B-XH-A_1x02_P2.50mm_Horizontal Update PCB routing
    [HappyAAC-Type-A.kicad_pcb, HappyAAC-Type-A.sch]
2021-06-06 Update gerber files and 3D pictures and pdf file of schematics
    [HappyAAC-Type-A-B_Cu.gbr, HappyAAC-Type-A-B_Mask.gbr, HappyAAC-Type-A-B_Paste.gbr, HappyAAC-Type-A-B_SilkS.gbr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]
2021-06-06 Update HappyAAC-Type-A.kicad_pcb.Mod.csv to keep new JST-HX-Connector and Header position
    [HappyAAC-Type-A.kicad_pcb.Mod.csv]
2021-06-07 Update Manual -- add Soldering guide for JST-HX Sockets
2021-06-09 Update user's manual - Soldering Guide finished
2021-06-09 Update BOM list
    [HappyAAC-Type-A.IO Table.ods]
2021-06-09 Update bill of material list
    [HappyAAC-Type-A.IO Table.ods]
2021-06-09 Add disclaimer and risc of Li-ion battery messages to user's manual
2021-06-10 Correct DO<->ROW1 D1<->ROW2 mapping notes and some messages on schematics
    [HappyAAC-Type-A.sch]
2021-06-10 Correct DO<->ROW1 D1<->ROW2 mapping in IO Table
    [HappyAAC-Type-A.IO Table.ods]
2021-06-17 Add sample code and SD card example for reference.
2021-06-22 1. Fix wrong PCB text for R1 (D15-->D9) on F.SilkS and B.SilkS 2. Update PCB version text to 2021.0611-1
    [HappyAAC-Type-A-B_Cu.gbr, HappyAAC-Type-A-B_Mask.gbr, HappyAAC-Type-A-B_Paste.gbr, HappyAAC-Type-A-B_SilkS.gbr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]
2021-07-14 Redo gerber files generating for revision 2d (because the GerberFiles folder has files for both rev 2c and 2d)
    [AACMaker-2c-job.gbrjob, AACMaker-Type-A-2c-job.gbrjob, HappyAAC-Type-A-2c-B_Cu.gbr, HappyAAC-Type-A-2c-B_Mask.gbr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]
2021-08-01 1. Fix footprint of J9 - battery connector, to keep connector's pin defination as text labels printed on the board. 2. Fix footprint of ICSP connector, let it's SilkS shape shows on the back side. 3.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
    [HappyAAC-Type-A-B_Cu.gbr, HappyAAC-Type-A-B_Mask.gbr, HappyAAC-Type-A-B_Paste.gbr, HappyAAC-Type-A-B_SilkS.gbr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]
